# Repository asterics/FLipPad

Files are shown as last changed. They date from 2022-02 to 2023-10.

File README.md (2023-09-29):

# FLipPad

The FLipPad (a.k.a. Flipable Touchpad) is a replacement for a normal PC mouse / keyboard / joystick. 
Instead of moving the mouse/joystick with your hand or pressing keys on a keyboard, the FLipPad can be controlled by very small finger movements.
Unlike a normal Touchpad, the FLipPad can act as mouse, keyboard or joystick - and it can even control bluetooth devices.
For mouse cursor movements, the sensitivity and the operational mode of the FLipPad can be configured, so that finger movements and gestures in the range of millimeters are sufficient to control a computer, smart phone or a complex game.

The clicking functionality is accomplished by tapping, by sip- and puff-activities or via external switches.
All settings and functions of the FLipPad can be tailored to specific capabilities or needs. 
Multiple settings can be stored into the device and changed via finger gestures or other user interactions.
Additional features like built-in environmental control via infrared, optional bluetooth-add-on module for controlling smartphones/tablets or complete software-based control of all functions via serial command interface make the FlipPad one of the most flexible alternative input devices available today.

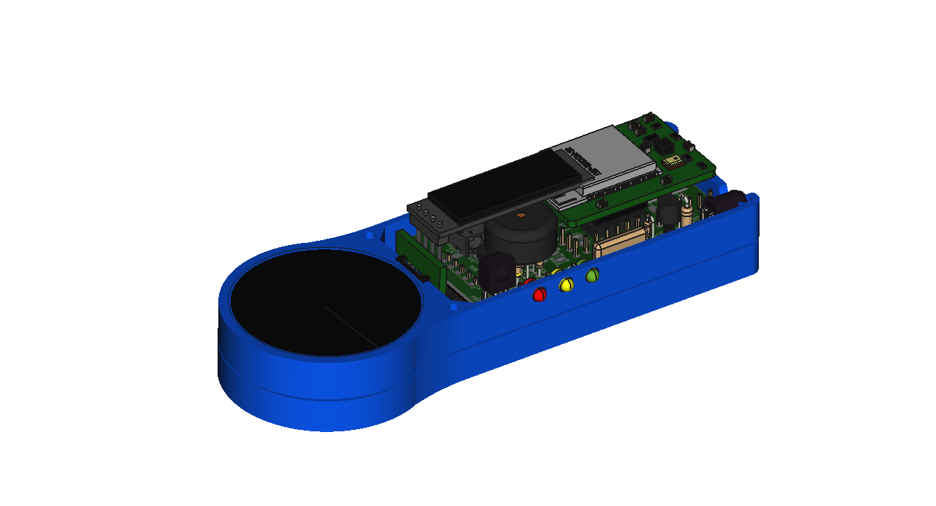
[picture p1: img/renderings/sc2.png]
FLipPad opened - rendered image


The FLipPad was created in course of the [TOM Abraham Accords challenge 2022](https://www.tomchallenge.org/), together with a need-knower who requested and tested this design.
It is based upon the [FlipMouse](https://github.com/asterics/FLipMouse) - a mouth-controller which is also available as Open Source project / DIY-construction kit!

# Software (firmware and configuration manager)

The FLipPad firmware is based on the Arduino/Teensyduino framework. The firmware implements a composite USB HID device (mouse, keyboard, joystick and a serial port in one device).
The mouse and keyboard device classes are used to transmit different keys or mouse actions to the host device. The serial port is used configure the FLipPad (or even use it as a mouse simulator via AT commands).
Multiple configuration settings can be saved (stored in an EEPROM module) and changed via desired user actions.

## Configuration Manager

All settings of the FLipPad can be changed via the [FlipPad Configuration manager](https://flippad.asterics.eu)  
Using the configuration manager in the Chrome web browser, you can assign different actions to all user inputs of the FLipPad.
The Configuration mananger can also be used to update the firmware of the FlipPad and the optional Bluetooth module.

More Information can be found in the user manual: 
* [user manual (english version)](https://github.com/asterics/FLipPad/blob/main/Documentation/UserManual/FLipPadUserManual.md)
* [user manual (german version)](https://github.com/asterics/FLipPad/blob/main/Documentation/UserManual/FLipPadAnwendungsanleitung.md)

## Building the firmware
In order to build the firmware following prerequisites and dependencies must be installed:
* the [Arduino IDE](https://www.arduino.cc/en/software) - use either IDE1 version 1.8.x or IDE2 verison 2.0.x
* the [Teensyduino](https://www.pjrc.com/teensy/td_download.html) add-on (must be compatible with the Arduino IDE version)
* the [SSD1306Ascii](https://github.com/greiman/SSD1306Ascii) library by Bill Greiman (can be installed using Arduino IDE's library manager)
* **important:** in the header file WireKinetis.h (Teensy Wire-library implemenation), *uncomment* the line `//#define WIRE_IMPLEMENT_WIRE1` - should be line number 50, see [here](https://github.com/PaulStoffregen/Wire/blob/2499ec67c2128629ee33697804f8650180293597/WireKinetis.h#L50). 
(This is needed to implement the Wire1 interface, which is disabled by default for the TeensyLC microcontroller in order to save memory.) 
  * If you are using a 1.8.x IDE version under Windows, the file is located inside a subfolder of the Arduino IDE installation, e.g.
`C:/Program Files (x86)/Arduino-1.8.19/hardware/teensy/avr/libraries/Wire/WireKinetis.h` 
  * If you are using a 2.0.x IDE version under Windows, the file is located inside a subfolder of Application Data, e.g.
`C:/Users/<YourName>/AppData/Local/Arduino15/packages/teensy/hardware/avr/1.58.0/libraries/Wire/WireKinetis.h`
* select the *board* 'Teensy LC' in the Arduino IDE tools menu
* select the *USB-type* 'Serial+Keyboard+Mouse+Joystick'  in the Arduino IDE tools menu
* select the correct *Port* after connecting the TeensyLC to your system
* compile and upload the firmware 

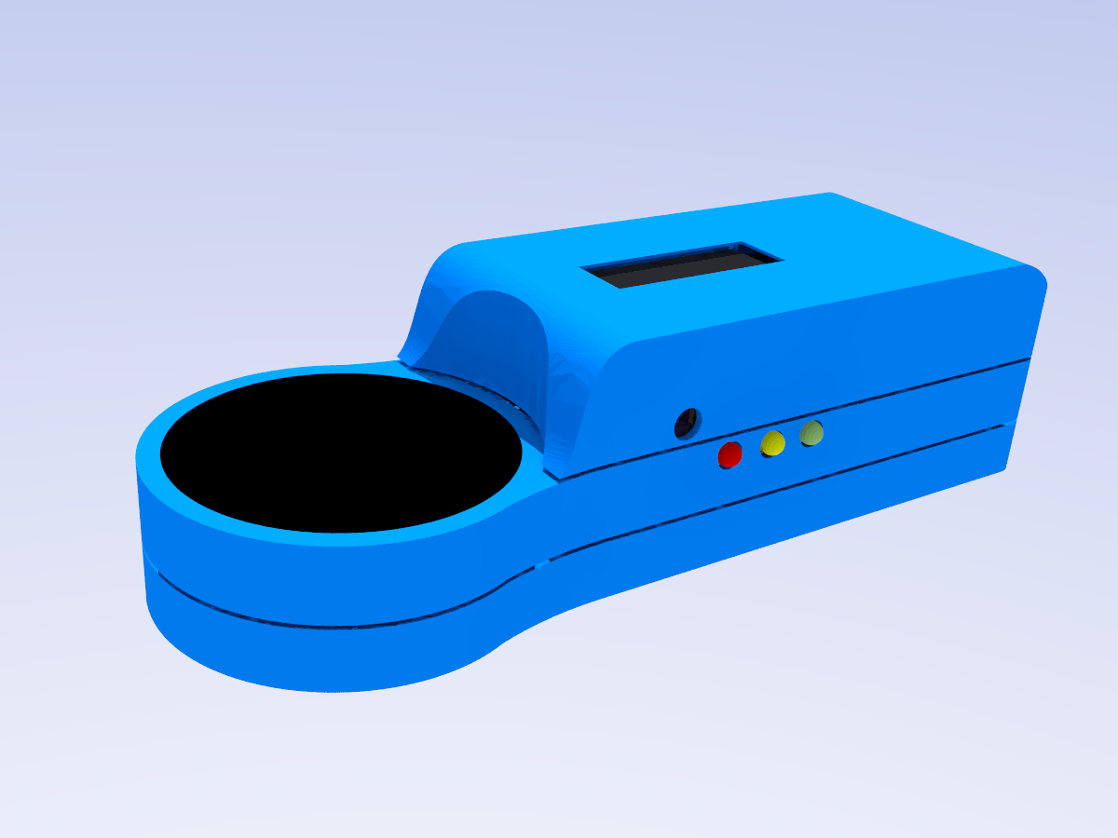
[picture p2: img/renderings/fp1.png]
FLipPad with 3d-printed enclosure - rendered image


# Links and Credits

Most of the work for the FLipPad has been accomplished at the UAS Technikum Wien in course of the R&D-project *WBT* (MA23 project 26-02), which has been supported by the [City of Vienna](https://www.wien.gv.at/kontakte/ma23/index.html),
see: [Webpage WBT project](https://wbt.wien).

Have a look at the [AsTeRICS Foundation homepage](https://www.asterics-foundation.org) and our other Open Source AT projects:

* AsTeRICS: [AsTeRICS framework homepage](http://www.asterics.eu), [AsTeRICS framework GitHub](https://github.com/asterics/AsTeRICS): The AsTeRICS framework provides a much higher flexibility for building assistive solutions. 
The FLipMouse is also AsTeRICS compatible, so it is possible to use the raw input data for a different assistive solution.

* FLipMouse: [The FLipMouse controller](https://github.com/asterics/FLipMouse): an open source alternative input device for controlling computers and mobile devices with minimal muscle movement.

* FABI: [FABI: Flexible Assistive Button Interface GitHub](https://github.com/asterics/FABI): The Flexible Assistive Button Interface (FABI) provides basically the same control methods (mouse, clicking, keyboard,...), but the input
is limited to simple buttons.

* AsTeRICS Grid: [Asterics Grid AAC Web-App](https://grid.asterics.eu): an open source, cross plattform communicator / talker for Augmented and Alternative Communication (AAC).

# Support us
Please support the development of FLipPad by donating to the AsTeRICS Foundation:

<div>
<a title="Donate with PayPal" href="https://www.paypal.com/donate/?hosted_button_id=38AJJNS427MJ2" target="_blank" style="margin-right:3em">
</a>
<span>&nbsp;&nbsp;&nbsp;</span>
<a title="Donate at opencollective.com" href="https://opencollective.com/asterics-foundation" target="_blank">
</a>
</div>

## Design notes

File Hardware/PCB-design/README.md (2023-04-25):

# FLipPad PCB

The main PCB of the FlipPad is compatible with the FLipMouse V2 PCB,
please refer to: https://github.com/asterics/FLipMouse-v2/tree/master/Hardware/PCB-design/Lipmouse_Teensy

__Note:__ Although the PCB is the same, some parts are not placed on the FLipPad PCB. Please refer to the Construction Manual: 
https://github.com/asterics/FLipPad/blob/master/ConstructionKit/ConstructionManual.pdf

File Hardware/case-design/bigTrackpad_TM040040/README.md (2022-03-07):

# Case for TM040040 trackpad

This case version is used for the bigger trackpad from Cirque.
The FreeCAD design in this folder is used for changing/adapting the case.
For renderings and animations, the STL files from this repository are transfered to the
FreeCAD project in the construction manual repo: https://github.com/benjaminaigner/ConstructionManual-FLipPad

To ease up the case design process, the PCBs and external parts are placed in the FreeCAD design.

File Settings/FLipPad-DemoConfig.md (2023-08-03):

## Basic information
This configuration offers 4 modes (slots), demonstrating basic FlipPad settings and operation.
The modes can be changed by pressing Button1.

## Slot1 - "Mouse"
- controls mouse cursor via USB interface
- create mouse clicks via external buttons (button2: hold left mouse button / button3: click right mouse button)
- uses joystick mode (return finger to first touch point or lift finger to stop moving)

## Slot2 - "MousePad"
- controls mouse cursor via USB interface
- create mouse clicks via external buttons (button2: hold left mouse button / button3: click right mouse button)
- uses pad mode (finger movement = cursor movement)

## Slot3 - "MouseBT"
- controls mouse cursor via BT interface 
- uses joystick mode (return finger to first touch point or lift finger to stop moving)
- create mouse clicks via external buttons (button2: hold left mouse button / button3: click right mouse button)
- note that the BT-module must be installed and paired with a BT-capable device

## Slot4 - "Key"
- finger movement creates cursor keys (up / down / left / right) via USB interface
- button2: hold Space key
- button3: hold enter key
- uses sticky pad mode (last finger movement determines key, keys remain sticky)

## for all slots:
- Button1 (internal button): load next slot

## Please note:
- The position correction which is applied after taps and finger gestures only works correctly if the feature "enhance mouse pointer precision" is deactivated, please check the mouse pointer settings of your operating system. Also the overall mouse pointer speed may be adjusted there.

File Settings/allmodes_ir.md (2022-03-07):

## Basic information
This configuration offers 5 modes (slots) for different mouse-pointer, keyboard and infrared actions.
The modes can be changed by triple taps or by pressing Button1/Button3.

## Slot1 - "StickMode"
- controls mouse cursor via USB interface
- uses joystick mode (return finger to first touch point to stop moving)

## Slot2 - "PadMode"
- controls mouse cursor via USB interface
- uses pad mode (finger movement = cursor movement)

## Slot3 - "Phone"
- controls mouse cursor via BT interface 
- uses pad mode (finger movement = cursor movement)
- another tap+down gesture or pressing external button3 creates the keyboard shortcut KEY_GUI + KEY_BACKSPACE which acctivates the Home/Back button in many Android phones
- note that the BT-module must be installed and paired with a BT-capable device

## Slot4 - "GameKey"
- finger movement creates cursor keys (up / down / left / right) via USB interface
- tap creates space key
- uses sticky pad mode (last finger movement determines key, keys remain sticky)

## Slot5 - "TVRemote"
- finger movement up/down: play ir commands "ChnUp" / "ChnDwn" for changing the TV channel 
- finger movement left/right: play ir commands "VolUp" / "VolDwn" for changing the TV volume 

## for all slots:
- Button1 (internal button), Button3 or TripleTap: load next slot
- Button2 or Sip: hold left mouse button (in Slot4: Space Key)
- Puff: click right mouse button (in Slot4: Enter Key)

## Please note:
- The position correction which is applied after taps and finger gestures only works correctly if the feature "enhance mouse pointer precision" is deactivated, please check the mouse pointer settings of your operating system. Also the overall mouse pointer speed may be adjusted there.
- The IR commands "ChnUp", "ChnDwn", "VolUp" and "VolDwn" must be recorded for your device via the WebGui before you can use the "TVremote" actions

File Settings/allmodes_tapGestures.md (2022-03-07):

## Basic information
This configuration offers 4 modes (slots) for different mouse-pointer or keyboard actions.
The modes can be changed by finger gestures (tap + movement), by triple taps or by pressing Button1.

## Slot1 - "StickMode" (double tap + up)
- controls mouse cursor via USB interface
- uses joystick mode (return finger to first touch point to stop moving)

## Slot2 - "PadMode"  (double tap + right)
- controls mouse cursor via USB interface
- uses pad mode (finger movement = cursor movement)

## Slot3 - "Phone" (double tap + down)
- controls mouse cursor via BT interface 
- uses pad mode (finger movement = cursor movement)
- another tap+down gesture or pressing external button3 creates the keyboard shortcut KEY_GUI + KEY_BACKSPACE which acctivates the Home/Back button in many Android phones
- note that the BT-module must be installed and paired with a BT-capable device

## Slot4 - "GameKey" (double tap + left)
- finger movement creates cursor keys (up / down / left / right) via USB interface
- tap creates space key
- uses pad mode (last finger movement determines key)

## for all slots:
- Button 1 (internal button) or tripe tap = load next slot
- Button 2, Sip = hold left mouse button (in Slot4: Space Key)
- Puff = click right mouse button (in Slot4: Enter Key)

## Please note:
The position correction which is applied after taps and finger gestures only works correctly if the feature "enhance mouse pointer precision" is deactivated, 
please check the mouse pointer settings of your operating system. Also the overall mouse pointer speed may be adjusted there.

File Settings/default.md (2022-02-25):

## Basic information
This configuration is the default configuration of the FlipPad.
It offers 4 modes (slots) for different mouse-pointer or keyboard actions.
The modes can be changed by finger gestures (double tap + movement) or by pressing Button1/Button3.

## Slot1 - "StickMode" (double tap + up)
- controls mouse cursor via USB interface
- uses joystick mode (return finger to first touch point to stop moving)

## Slot2 - "PadMode"  (double tap + right)
- controls mouse cursor via USB interface
- uses pad mode (finger movement = cursor movement)

## Slot3 - "Phone" (double tap + down)
- controls mouse cursor via BT interface 
- uses pad mode (finger movement = cursor movement)
- a tap + down gesture creates the keyboard shortcut KEY_GUI + KEY_BACKSPACE which acctivates the Home/Back button in many Android phones
- note that the BT-module must be installed and paired with a BT-capable device

## Slot4 - "GameKey" (double tap + left)
- finger movement creates cursor keys (up / down / left / right) via USB interface
- tap creates space key
- uses pad mode (last finger movement determines key)

## for all slots:
- Button 1 (internal button), Button3 = load next slot
- Button 2, Sip = hold left mouse button (in Slot4: Space Key)
- Puff = click right mouse button (in Slot4: Enter Key)

## Please note:
The position correction which is applied after taps and finger gestures only works correctly if the feature "enhance mouse pointer precision" is deactivated, 
please check the mouse pointer settings of your operating system. Also the overall mouse pointer speed may be adjusted there.

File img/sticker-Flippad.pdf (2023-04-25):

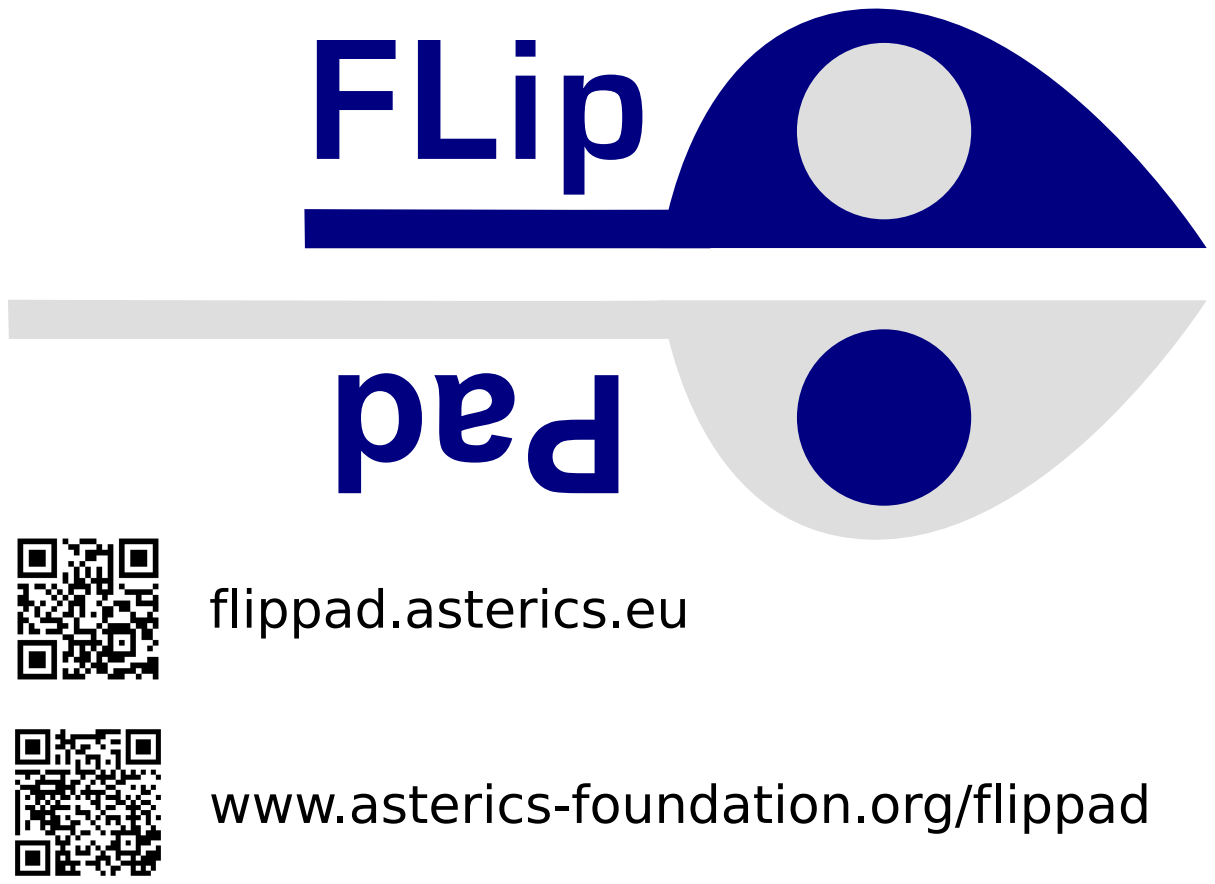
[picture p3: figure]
www.asterics-foundation.org/flippad; flippad.asterics.eu

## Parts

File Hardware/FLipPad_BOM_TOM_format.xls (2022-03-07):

Nr. | Description | Material | Manufacturing Technology | Dimensions | Quantity | Supplier / Purchase Link
1 | Main PCB | FR4 | PCB manufacturing | 61x32x1.6 | 1 | aisler.net (or other PCB manufacturer)
2 | 2x5 2.54mm pin header (male) |  |  | 13x5x16 | 1 | Digikey.com: 952-2124-ND
3 | 100nF ceramic capacitor, 2.5mm pin spacing |  |  | 3x2x3 | 2 | Digikey.com: 478-4855-ND
4 | 1x4 2.54mm pin header (male) |  |  | 13x2.5x16 | 1 | Digikey.com: 732-5318-ND
5 | 1x14 2.54mm pin header (male) |  |  | 36x2.5x16 | 2 | Digikey.com: 732-5325-ND
6 | TeensyLC |  |  | 36x18x4 | 1 | Digikey.com: 1528-2254-ND
7 | 3.5mm jack plugs, 4pin |  |  | 16x7x5 | 2 | Farnell.com: 1216979
8 | SIP resistor network 220R |  |  | 12x2x4 | 1 | Digikey.com: 4605X-101-221LF-ND
9 | 24LC256 EEPROM |  |  | 9x8x4 | 1 | Digikey.com: 24LC256-I/P-ND
10 | TSOP4838 IR receiver |  |  | 7x4x8 | 1 | Digikey.com: TSOP4838-ND
11 | BS170 N-channel MOSFET TO92 |  |  | 5x4x5 | 1 | Digikey.com: BS170_D75ZCT-ND
12 | push button long actuator |  |  | 12x7x7 | 1 | Digikey.com: P10884S-ND
13 | push button short actuator |  |  | 7x7x7 | 1 | Digikey.com: 450-1656-ND
14 | THT resistor 1/8W; 4k7; blue |  |  | 3x1x1 | 4 | Farnell.com: 9343253
15 | THT resistor 1/2W; 12R; brown |  |  | 9x2x2 | 1 | Digikey.com: CFR-50JB-52-12R
16 | 3mm LEDs, red, gren & yellow |  |  | 3x3x5 | 3 | Digikey.com: 160-1708-ND, 160-1946-ND, 160-1710-ND
17 | 5mm IR LED |  |  | 5x5x8 | 1 | Digikey.com: 751-1204-ND
18 | buzzer |  |  | 16x16x8 | 1 | Farnell.com: 1300026
19 | pin spacer | PLA | 3D printed | 3x3x14 | 1 | Self-printed
20 | 1x5 2.54mm pin header (male); 90° |  |  | 9x5x6 | 1 | Digikey.com: 732-5338-ND
21 | Fully assembled FFC adapter PCB |  |  | 19x16x3 | 1 | aisler.net (or other PCB manufacturer with assembly)
22 | 100mm 12pin FFC cable, 0.5mm spacing |  |  | 100x10x0.1 | 1 | Mouser.com: 538-15166-0123
23 | Case-bottom ; bottom part of case | PLA | 3D printed | 36x120x7 | 1 | Self-printed
24 | hot shoe 3/8“ screw | steel |  | 15x15x25 | 1 | https://de.aliexpress.com/item/1005002037418382.html
25 | Case-base ; middle part of case | PLA | 3D printed | 36x120x9 | 1 | Self-printed
26 | OLED 0.91“ SSD1306 |  |  | 38x12x3 | 1 | https://de.aliexpress.com/item/32672229793.html
27 | TM035035 Cirque Trackpad |  |  | 36x36x10 | 1 | Mouser.com: 355-TM0350352024-003
28 | Case-top ; top part of case | PLA | 3D printed | 77x37x18 | 1 | Self-printed
29 | M2x16 (countersunk head) | steel |  | 3x3x17 | 1 | https://de.aliexpress.com/item/1005001971590776.html
30 | Optional: ESP32 addon |  |  | 34x24x12 | 1 | aisler.net (or other PCB manufacturer with assembly)

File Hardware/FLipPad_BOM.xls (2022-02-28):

Device | Package | Parts | Description | Qty | Farnell.com | Digikey.com | RS-Components | aliexpress.com | Others | Pin count | critical mounting Position/direction | Price Single | Price 100 Pieces | all prices excl. VAT (€ if not otherwise noted)
FLIpmouse – electronic parts
31-XX | B3F-31XX | S1 | TE – SPST-NO, short button | 1 | 2452343 | 450-1656-ND | 718-2370 |  |  | 4 | yes | 0.086 | 0.078
31-XX | B3F-31XX | S2 | EVQPF108K SWITCH, long Button | 1 | 2079506 | P10884S-ND | 756-1599 |  |  | 4 | yes | 0.18 | 0.13
FE05-1 | FE05-1 | SV1 | MALE HEADER, 90°, 1x5 | 1 | 2356179 | 732-5338-ND | 828-1667 |  |  | 5 | yes | 0.37 | 0.208
LED3MM | LED3MM | LED1 | LED red – MCL514PD | 1 | 1581128 | 160-1708-ND |  |  |  | 2 | yes | 0.153 | 0.0689
LED3MM | LED3MM | LED2 | LED yellow – MCL514YD | 1 | 1581131 | 160-1946-ND |  |  |  | 2 | yes | 0.249 | 0.0848
LED3MM | LED3MM | LED3 | LED green – MCL514GD | 1 | 1581130 | 160-1710-ND |  |  |  | 2 | yes | 0.198 | 0.0848
MA05-2 | MA05-2 | AUX | MALE HEADER, 2x5; Harwin M20 | 1 | 1022236 | 952-2124-ND |  |  |  | 10 | - | 0.258 | 0.222
RN04 | RN-5 | RN1 | Resistor network, 220R | 1 | 2333623 | 4605X-101-221LF-ND |  |  |  | 5 | yes | 0.362 | 0.153
TeensyLC – pin header | MA14-1 | -- | MALE HEADER, 1x14 | 2 | 2356164 | 732-5325-ND |  |  | Alternative: 2356174 (farnell) / 732-5333-ND (digikey) For all 3 pin headers | 14 | - | 1.77 | 0.896
TeensyLC – pin header | MA05-1 | -- | MALE HEADER, 1x5 | 1 | 2356157 | 732-5318-ND |  |  |  | 5 | - | 0 | 0
C-EU025-025X050 | C025-025X050 | C1,C2 | 100nF capacitor | 2 | 2112751 | 478-4855-ND |  |  |  | 2 | - | 0.21 | 0.121
1503_02 | 1503_02 | X1,X2 | Jack plugs JISC 6560 | 2 | 1216979 |  |  |  |  | 4 | yes | 2.82 | 2.28
24LC256P | 24LC256P | IC1 | I2C EEPROM | 1 | 9757970 | 24LC256-I/P-ND | 454-371 |  |  | 8 | yes | 0.84 | 0.681
R-EU_0309/V | 0309V | R1,R2,R3,R11 | 4k7, blue, | 4 | 9343253 |  |  |  |  | 2 | - | 0.174 | 0.0765
LED5MM | LED5MM | LED5 | LED | 1 | 3152856 | 751-1204-ND | 699-7635 (or 50pcs: 818-7663) |  |  | 2 | yes | 0.122 | 0.104
R-EU_0309/V | 0309V | R12 | 12R, min 0.25W | 1 | 9338420 | CFR-50JB-52-12R |  |  |  | 2 | - | 0.061 | 0.04
Piezo buzzer | EFBAA40D101 | SG1 | piezo buzzer | 1 | 1300026 |  | 457-011 |  | Cheaper at rs-components | 2 | - | 0.61 | 0.51
TSOP4838 | TSOP2XXX | U3 | TSOP4838 | 1 | 4913190 | TSOP4838-ND | 708-5115 (or 90pcs: 919-0014) |  |  | 3 | yes | 1.06 | 0.539
BS170 | TO-92 | Q1 | N-MOS FET, BS170 | 1 | 2453831 | BS170_D75ZCT-ND | 671-4736 |  |  | 3 | yes | 0.138 | 0.138
FlipPad daughterboard & mechanical parts
header 5pol | FE05-1 | SV1 | FEMALE HEADER, 1x5 | 1 |  | SAM1122-05-ND |  |  | Alternative: 9728910 (Farnell, for 7) | 5 | yes | 0.9028571429 | 0.75
Glide trackpad (TM035035) |  |  |  | 1 |  |  |  |  | mouser: 355-TM0350352024-003 |  |  | 7.7 | 5.5
glide_adapter – PCB |  |  |  | 1 |  |  |  |  | see the glide_adapter PCB & BOM |  |  | 5 | 1
OLED SSD1306 – 0.91“ |  |  |  | 1 |  |  |  |  | order at Aliexpress, Azdelivery or Amazon |  |  | 1 | 0.8
Spacer – adjusting pin header/LEDs | -- | -- | -- | 1 |  |  |  |  | self printed | 5 | - | 0.35 | 0.2
Flipmouse Teensy, PCB | -- | -- | -- | 1 |  |  |  |  | PCBPool, etc. | - | - | 8 | 3.44
TEENSYLC | TEENSY_3.1_BASIC | TEENSYLC | TeensyLC | 1 |  | 1568-1233-ND |  |  | watterott.com (or: PJRC.com) | 33 | yes | 12.5 | 12.5
Hot shoe adapter (mounting) | -- | -- | -- | 1 |  |  |  | Search for „3/8" hot shoe mount“ | Amazon: B00RSXM3U2 | - | - | 2.18 | 1.2
USB cable | -- | -- | -- | 1 | -- | -- |  | Search for „MicroUSB cable 1m“ |  | -- | -- | 2 | 2
USB stick | -- | -- | -- | 1 | -- | -- |  | Search for „8GB USB Stick orange“ |  | -- | -- | 4 | 3
Packaging | -- | -- | -- | 1 | -- | -- |  | -- | -- | -- | -- | 6 | 6
Parts ONLY for 3D printed case
M2x16 screw | -- | -- | -- | 2 | 7070585 | 36-29341-ND |  |  |  | - | - | 5.68 | 0.2272
3D printed case (3 parts) | -- | -- | -- | 1 |  |  |  |  |  | - | - | 3 | 2
 |  |  |  |  |  |  |  |  |  |  | Sum: | 67.97 | 45.03
 |  |  |  |  |  |  |  |  |  |  | Shipping costs: | 25.00 | 0.25
Packing material (box for kit) |  | Stülpkarton |  | 1 |  |  |  |  | Ratioform 167-5w |  |  | 1.69 | 1.39
Packing material (send carton) |  | Verpackungskarton |  | 1 |  |  |  |  | Ratioform W129 |  |  | 0.55 | 0.51
 |  |  |  |  |  |  |  |  |  |  | TOTAL (3D print): | 114.26 | 56.62
 |  |  |  |  |  |  |  |  |  |  | Including 20% VAT

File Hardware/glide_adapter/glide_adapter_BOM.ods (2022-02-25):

Reference | Value | Footprint | Datasheet | Mouser | Notes
J2 | Conn_01x12_Female | Connector_FFC-FPC:Hirose_FH12-12S-0.5SH_1x12-1MP_P0.50mm_Horizontal | ~ | 798-FH12-12S-0.5SH55
J1 | Conn_01x05_Female | Connector_PinSocket_2.54mm:PinSocket_1x05_P2.54mm_Vertical | ~ | DON'T ORDER (437-8018700510001101) | normally, a connector is available in your lab or the FlipMouse construction kit.
R1,R2 | 4k7 | Resistor_SMD:R_0805_2012Metric_Pad1.20x1.40mm_HandSolder | ~ | 603-AC0805FR-7W4K7
J3 | Conn_01x04_Female | Connector_Harwin:Harwin_M20-89004xx_1x04_P2.54mm_Horizontal | ~ | 801-87-004-40-002101
C1 | 1u | Capacitor_SMD:C_0805_2012Metric_Pad1.18x1.45mm_HandSolder | ~ | 710-885012207051
-- | Trackpad | TM035035-2024-003 (currently only available case) |  | 355-TM0350352024-003 | Select one here: https://www.mouser.at/new/cirque/glidepoint-circle-trackpads/
 | FFC cable | FPC cable, 12pol. Same side contacts, 76mm |  | 538-15166-0121

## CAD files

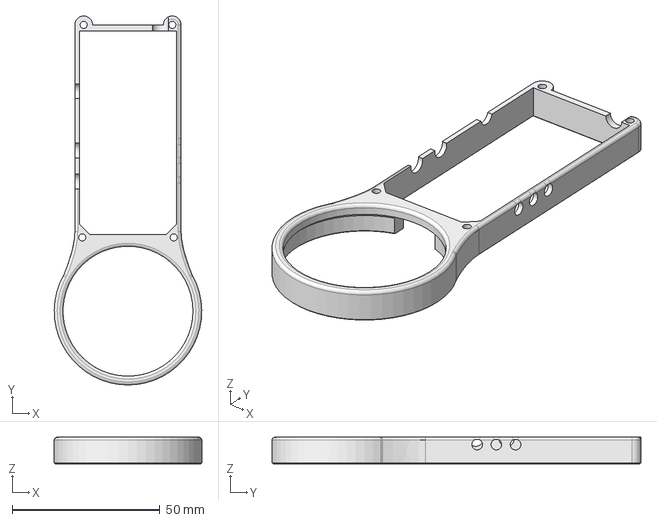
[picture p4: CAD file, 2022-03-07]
Hardware/case-design/bigTrackpad_TM040040/case_TM040040.FCStd
50.0 x 125.0 x 9.00 mm

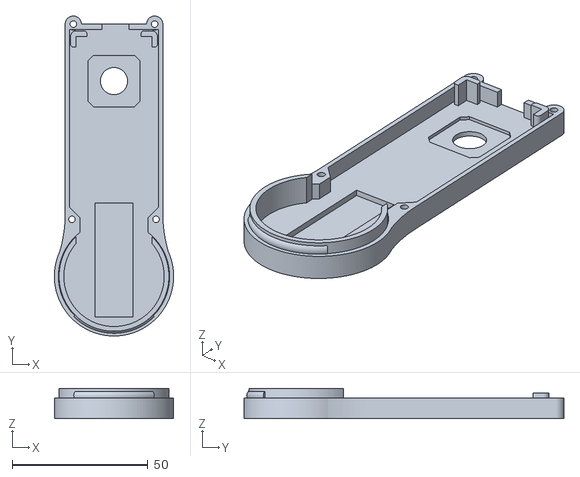
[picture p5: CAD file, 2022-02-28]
Hardware/case-design/smallTrackpad_TM035035/case_TM035035-bottom.stl
44.0 x 118.0 x 11.1

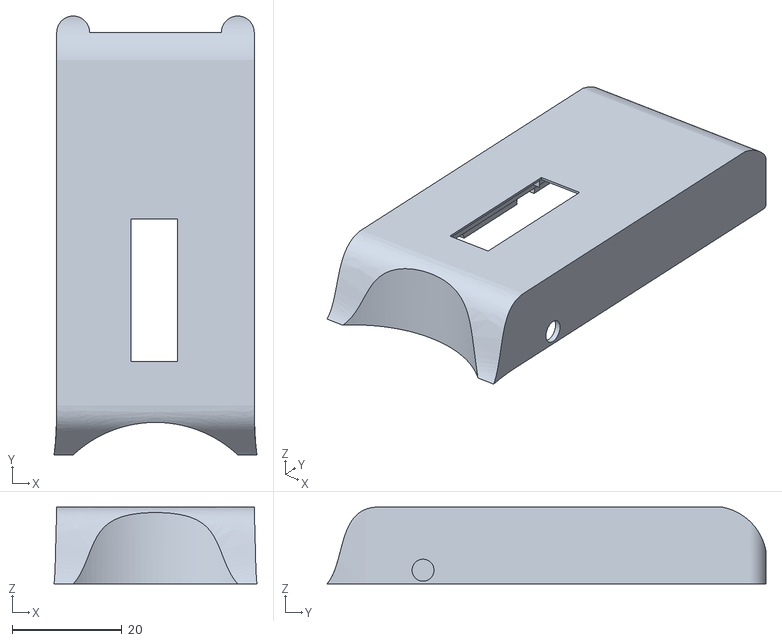
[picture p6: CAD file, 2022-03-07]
Hardware/case-design/bigTrackpad_TM040040/case_TM040040-top.stl
37.0 x 80.0 x 14.0

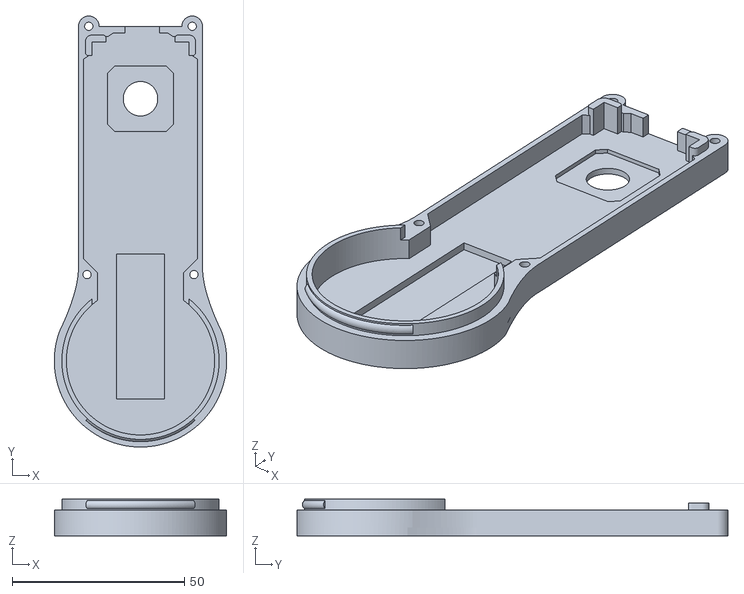
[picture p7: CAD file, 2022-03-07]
Hardware/case-design/bigTrackpad_TM040040/case_TM040040-bottom.stl
50.0 x 125.0 x 10.7

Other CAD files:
Hardware/case-design/bigTrackpad_TM040040/case_TM040040-base.stl

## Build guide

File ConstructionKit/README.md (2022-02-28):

# ConstructionManual

This construction manual contains instructions how to build the FlipPad.

**Have fun !!**

## Sources

Due to the size of the raw material, the sources for the PDF manual are located here: https://github.com/benjaminaigner/ConstructionManual-FLipPad

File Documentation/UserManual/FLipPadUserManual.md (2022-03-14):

# FLipPad - Finger Trackpad

**User Manual v3.1, AsTeRICS Foundation**

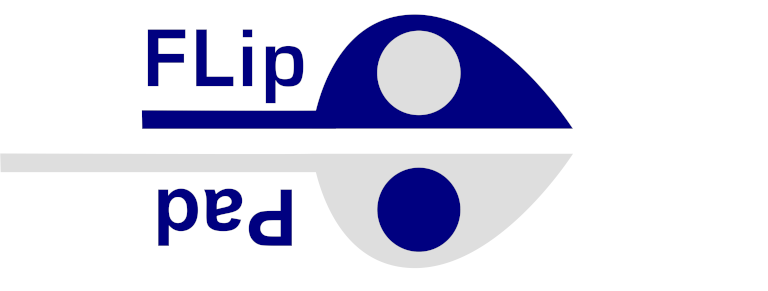
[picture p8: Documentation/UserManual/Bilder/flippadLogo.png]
FLipPadLogo


**Table of Contents**

[TOC]

____

# Preface

The FLipPad is an open source Assistive Technology module which is developed at the [University of Applied Sciences Technikum Wien](https://www.technikum-wien.at) and delivered as a DIY-construction kit by the [AsTeRICS Foundation](https://asterics-foundation.org). The FLipPad allows people who cannot use standard computer input devices to control a computer mouse cursor or a joystick as well as typing desired keyboard keys or using infrared remote controls. The FLipPad device can be actuated with minimal finger movements and/or external buttons. Sip & puff actuation is possible, but optional.

The FLipPad can be configured via a web-based configuration application which is called *configuration manager* from now on. It can be found at the website [flippad.asterics.eu](https://flippad.asterics.eu). This user manual includes a description of the configuration manager and explains how to use  the different functions and features of the FLipPad. The FLipPad can be used on any Windows-, Mac- or Linux-computer without installation of special software, because it behaves like a standard mouse / joystick / keyboard device. By using the optional Bluetooth Add-On module, smart phones or tablet computers can be controlled - which will also be explained in this manual. 

All design files for the electronics and the 3D-printed enclosure - as well as the software source code - are available as open source and are distributed via the AsTeRICS Foundation website and via GitHub. The construction kit for the FLipPad can be purchased from [Hackerspaceshop.com](https://hackerspaceshop.com/collections/FLipPad). Detailed instructions are provided in the [FLipPad construction manual](https://github.com/asterics/FLipPad/blob/master/ConstructionKit/ConstructionManual.pdf). Have fun building and using your FLipPad!

The AsTeRICS Foundation

[www.asterics-foundation.org](https://asterics-foundation.org/)

# Hardware overview

The FLipPad is available with a 3D-printed enclosure. Design files for the 3D-printed case are provided in the [Github repository](https://github.com/asterics/FLipPad/tree/main/Hardware/case-design). The primary method for interacting with the FLipPad is the black trackpad, which can either be a 35mm or a 40mm type.

<p align="left" width="100%">
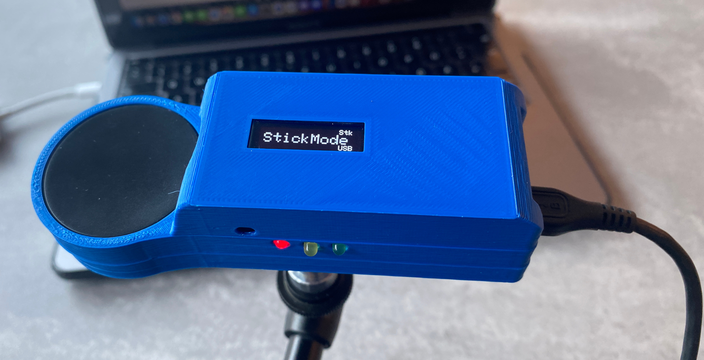
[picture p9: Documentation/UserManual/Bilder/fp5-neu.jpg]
    
</p>

*Figure 1*: The FLipPad device

Additionally, two external momentary switches can be attached to the jack plug connectors on the left side of the FLipPad enclosure and one button is already integrated on the device ("B1", see Figure 3).

**Users can interact with the FLipPad in several ways:**

1. by touching the trackpad and moving the finger
1. by tapping the trackpad once or more
2. by actuating (up to) 3 momentary switches / pushbuttons

**The hardware features of the FLipPad:** (see pictures at the bottom of this list)

(a)    One built-in switch (“Button 1 / B1”) on the device, e.g. to change the active configuration ("slot")

(b)    Two 3.5 mm jack plug sockets for attaching external switches to trigger additional functions (“Button 2 / B2” and “Button 3 / B3”)

(c)    3 Indicator Light Emitting Diodes (LEDs) for showing the active configuration, calibration procedure etc.

(d)    Universal infrared remote control receiver and transmitter

(e)    “Hot Shoe” Adapter for mounting to a Manfrotto Magic Arm or similar mounting system (3/8" screw)

(f)    Firmware upgrade via FLipPad web application on [FLipPad.asterics.eu](FLipPad.asterics.eu)

(g)    Optional add-on board for Bluetooth (e.g. to control smartphones or iOS devices)

<p align="left" width="100%">
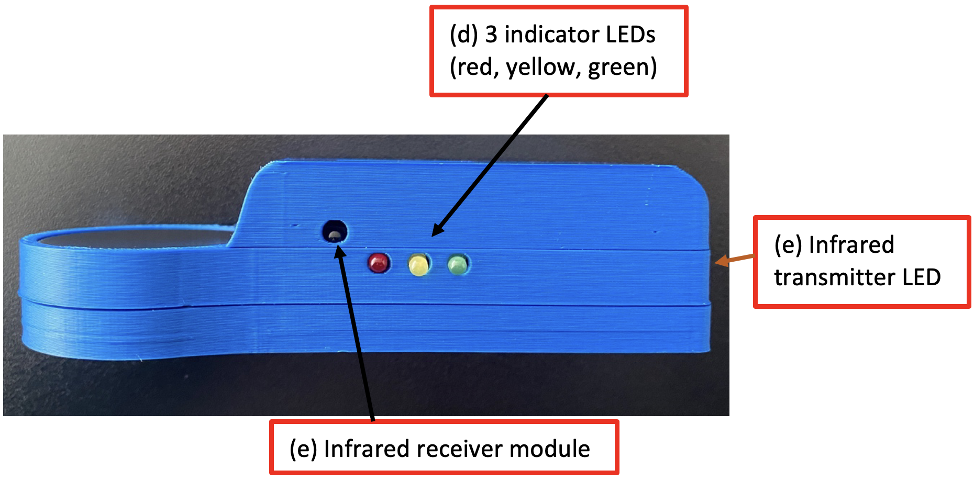
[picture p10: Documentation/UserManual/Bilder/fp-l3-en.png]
    
</p>

*Figure 2*: FLipPad right side

<p align="left" width="100%">
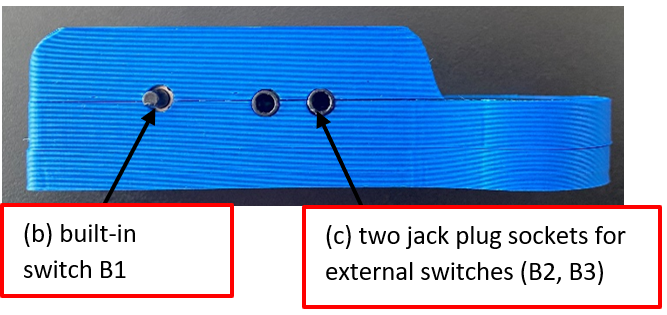
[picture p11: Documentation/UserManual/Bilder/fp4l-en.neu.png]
    
</p>

*Figure 3*: FLipPad left side

On the right side of the FLipPad enclosure, 3 LEDs indicate the current mode of operation (which can be changed to activate different speed settings or functional options). Furthermore, the Infrared (IR-) receiver module is accessible here. This modules can be used for recording arbitrary infrared remote control commands (for example to change volume or channel settings of a TV-set). The IR-signals can then be replayed from the IR-emitting diode at the rear side of the FLipPad.

The left side of the FLipPad gives access to a button (B1) which offers a configurable function (for example changing the operational mode).
Two 3,5mm Jack Plug sockets marked (B2) and (B3) allow the connection of external momentary switches. Standard switches with 3,5 mm mono jack plugs can be used.

## Bluetooth – Add-On Module

The optional Bluetooth Add-On module allows connection of the FLipPad as a Bluetooth mouse/keyboard to various mobile devices (smartphones, tablets, IOs devices). If this module is not contained in the DIY-Kit, it can be ordered individually from the AsTeRICS Foundation or built from the hardware design files available on Github (parts must be ordered individually). If you are interested in this feature, have a look at the [esp32_mouse_keyboard](https://github.com/asterics/esp32_mouse_keyboard/tree/master/hardware) repository where construction of the Add-On module is explained.

<p align="left" width="100%">
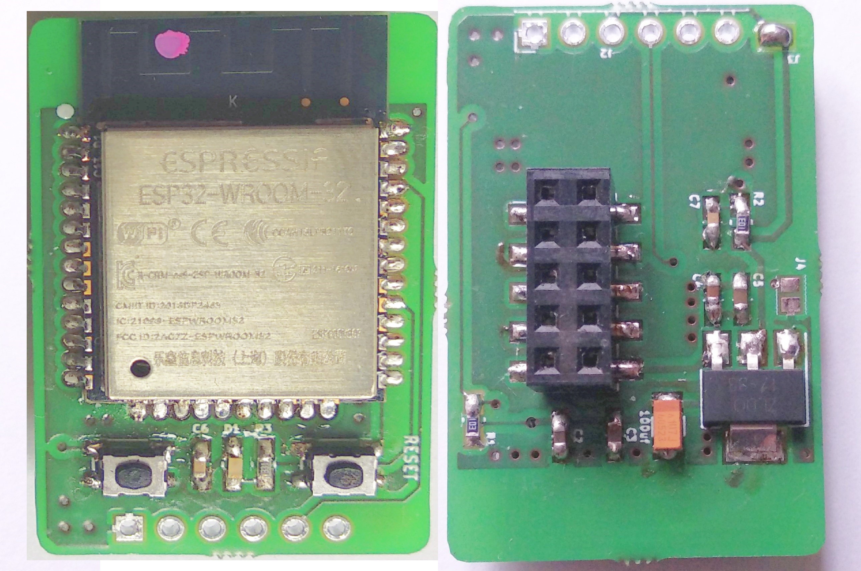
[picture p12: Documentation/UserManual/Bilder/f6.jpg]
    
</p>

*Figure 5*: Bluetooth Add-on Module

# Instructions for proper mounting and use

**1. Mount the FLipPad device appropriately for the user**
<p align="left" width="100%">
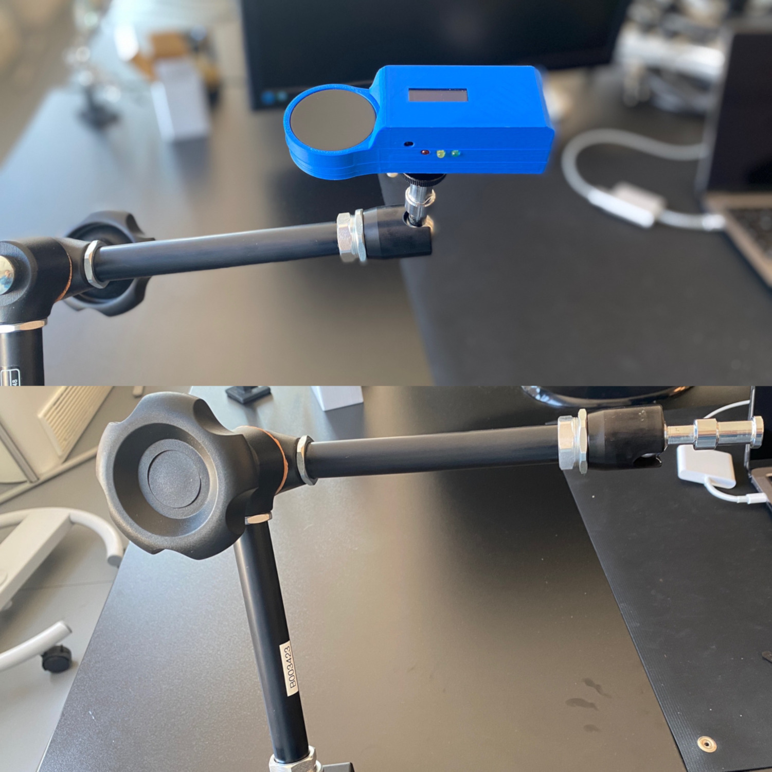
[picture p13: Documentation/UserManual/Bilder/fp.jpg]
    
</p>

*Figure 7*: Mounting the FLipPad

The picture shows a “[Manfrotto Magic Arm](https://www.manfrotto.com/global/magic-photo-arm-smart-centre-lever-and-flexible-extension-143n/)” + ”[SuperClamp](https://www.manfrotto.com/global/super-photo-clamp-without-stud-aluminium-035/)” mount combination. You could also use the [Manfrotto Gelenkarm](https://www.manfrotto.com/global/single-arm-2-section-196ab-2/) or any other kind of mounting solution which fits to the HotShoe-Adapter of the FLipPad. Be careful when attaching the mount to the 3/8” screw of the HotShoe-Adapter: hard forces might break the enclosure of the device. 

<p align="left" width="100%">
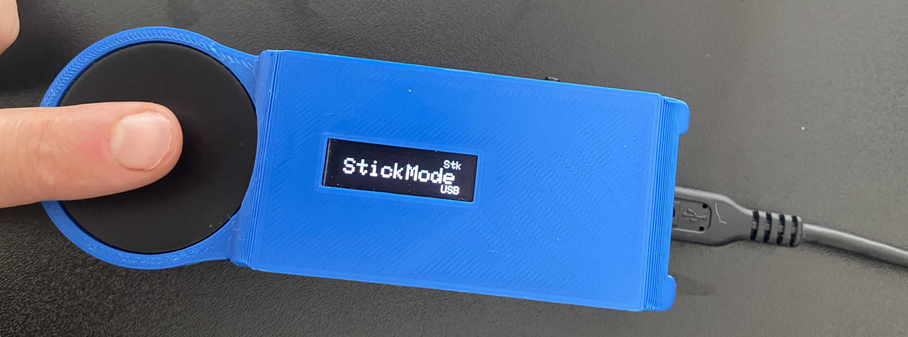
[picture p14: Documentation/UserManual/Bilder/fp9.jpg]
    
</p>

*Figure 9*: Using the FLipPad with fingers

If the user desires to actuate the FLipPad with a finger or the thumb the system appropriately so that the hand is in a resting position and the finger can touch the joystick without stress. Attach one or two additional external switches if desired, and mount the switches at suitable locations.

**2. Attaching the FLipPad to a Computer, Tablet or Smart Phone**

When connecting the FLipPad via the provided USB-micro cable, do not touch the mouthpiece as long as the LEDs are blinking (the initial blinking indicates the zero point calibration phase). Wait until the device is recognized by the computer, then touch the trackpad and move your finger to see if the device is working.

ball-switch

*Figure 11*: Connecting the FLipPad with the computer

**Please note** that every time you apply power to the FLipPad device (respectively when you plug it in) the **zero-calibration is performed which is indicated by blinking all 3 LEDs**. It is important that you do not touch the trackpad until the LEDs stopped blinking. 

#### Using the FLipPad with Smart Phones or Tablets that provide USB-OTG

The FLipPad should work with any operating system which supports USB HID (Mouse/Keyboard/Joystick) devices, such as Windows, Linux or MacOS. Several Android devices provide an USB port with USB-OTG (“on-the-go”) functionality. If your device supports “OTG” you can attach the FLipPad using an USB-OTG-adapter (see picture below) and it should work as a normal mouse (you will get a mouse cursor) or keyboard. You can test if your Android phone or tablet features the USB-OTG function with the “OTG checker” app.

<p align="left" width="100%">
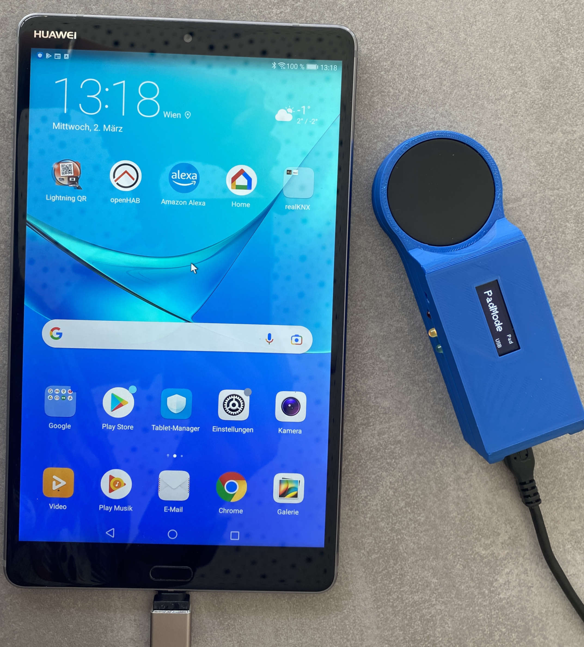
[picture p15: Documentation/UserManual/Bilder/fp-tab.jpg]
    
</p>

*Figure 12*: Using the FLipPad with the Smart Phone

#### Using the FLipPad via Bluetooth

The Bluetooth – Add-On-module for the FLipPad allows wireless mouse/keyboard control of computers, tablets and smart phones. Furthermore, iPhones or iPads can be used via VoiceOver & assistive switch support. For more information see chapter [*Using the Bluetooth Module*](https://github.com/asterics/FLipPad/blob/master/Documentation/UserManual/Markdown/FLipPadUserManual.md#using-the-bluetooth-module).

# The FLipPad Configuration Manager

The [FLipPad Configuration Manager](https://flippad.asterics.eu/index_pad.htm) offers a Graphical User Interface (GUI) to change and store settings of the FLipPad device so that all features and functions can be adapted to personal preferences and needs. **Currently, the Google Chrome browser (or a Chromium-based browser) must be used.** The Configuration Manager is accessible by entering the following website: **https://flippad.asterics.eu**. The FLipPad Configuration Manager sends and receives information from/to the FLipPad. This information transfer occurs through a communication port (COM port). 

The following figure shows the welcome page of the FLipPad Configuration Manager: 

<p align="left" width="100%">
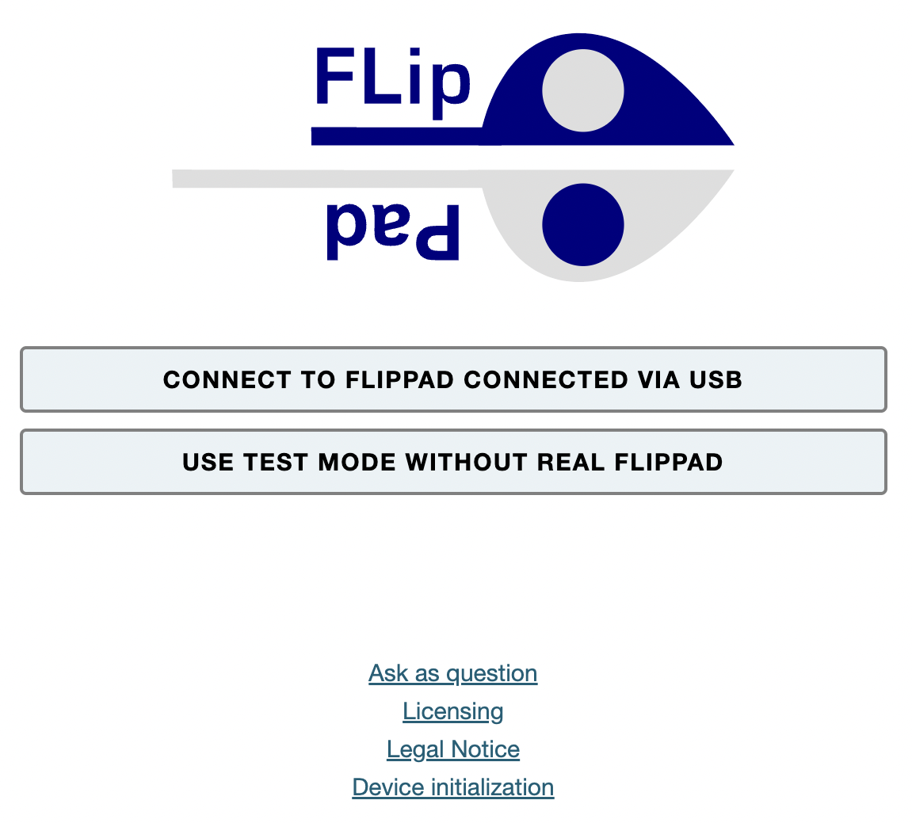
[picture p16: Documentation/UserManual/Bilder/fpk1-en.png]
    
</p>

*Figure 13: Welcome page of the FLipPad Configuration Manager*

### Connecting the FLipPad Device

To connect the device, follow these steps:

1. Make sure your device is connected to your computer via an USB port (see page "Instructions for proper mounting and use"). 
2. Click CONNECT TO FLIPPAD CONNECTED VIA USB and select the appropriate COM port (communication port) in the selection box. If the selection box appears empty, this means that no communication port has been detected. In this case, please reconnect the FLipPad device and wait for the COM port to be updated.
3. Once the COM port is selected, click the “Connect” button at the bottom of the selection box. 
4. After successful connection of the COM port, the main window (see Figure 14) will be displayed and you should see live feedback of the stick movement. The port status at the top right corner of the window will show “connected”.

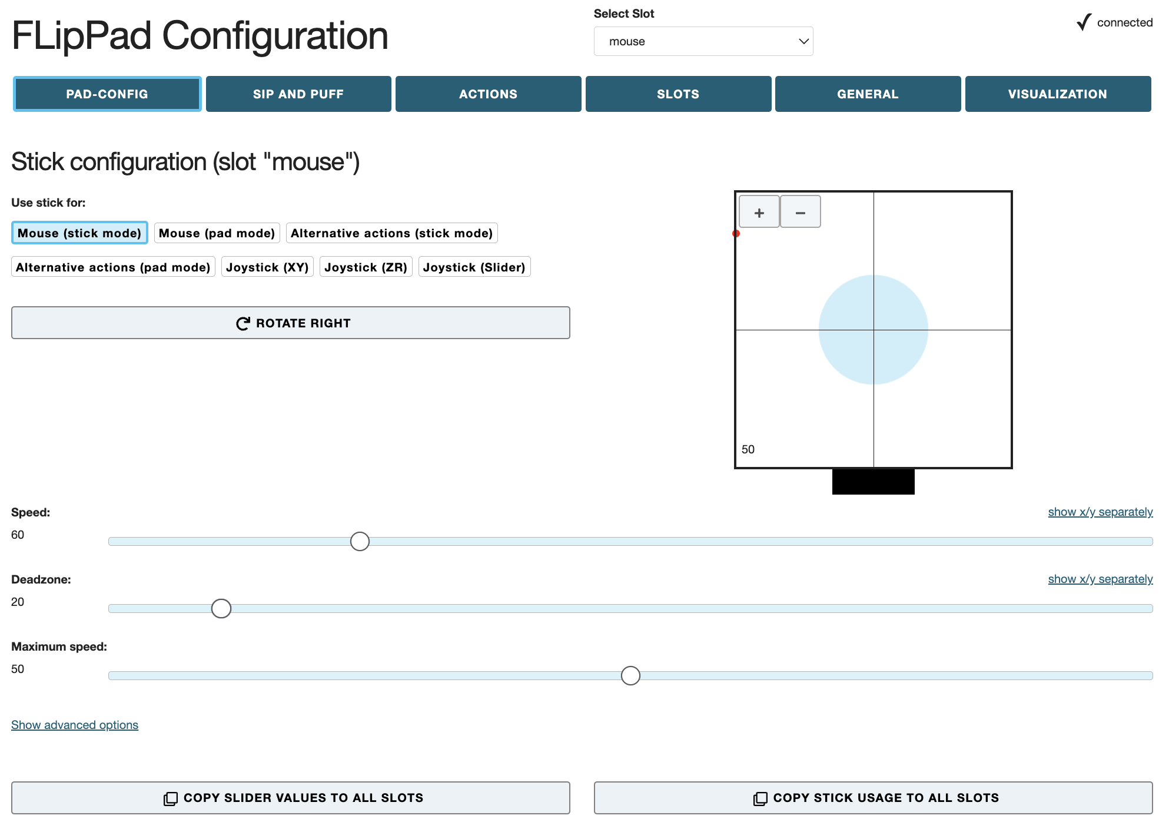
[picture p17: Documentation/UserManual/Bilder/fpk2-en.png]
ConfigManager


*Figure 14: FLipPad Configuration Manager*

## Changing Settings and Features

### Operational modes – “memory slots”

The FLipPad Configuration Manager allows adjustment of all important settings (operational modes). The settings are stored in individual **memory slots** (for example one slot for fast mouse operation, one slot for slow mouse operation, one slot for keyboard key generation etc.). All settings can be stored into (or loaded from) the FLipPad device. The settings can also be saved to (or loaded from) a file on your computer. 
Settings which were stored into the FLipPad stay valid also if the power supply / USB cable is removed. When the FLipPad is plugged in the next time, the settings will be available – also if you use another computer or operating system!

### PAD Configuration (Tab PAD-CONFIG)

Using the PAD-CONFIG tab of the FLipPad Configuration Manager, you will be able to change the *Speed, Deadzone* and *MaximumSpeed* of the FLipPad pad. Furthermore, you can change *Acceleration, Trackpad sensitivity*, *Maximum tap duration* and *Maximum duration of Tap + Slide gestures* - these settings are visible only if you activate *“Show advanced options”*. 

#### Define pad usage (“Use pad for”)

On the top of the PAD-CONFIG tab, the primary function of the pad can be chosen. By default, the pad is creating mouse cursor movements. However, the pad can also be used for alternative actions (such as pressing the key ‘A’ when the pad is pushed up), which can be specified in the ACTIONS tab (see section [*Assignment of different actions*](https://github.com/asterics/FLipPad/blob/master/Documentation/UserManual/Markdown/FLipPadUserManual.md#assignment-of-different-actions-tab-actions). Furthermore, the pad can emulate a real joystick or gamepad  (see section [*Using the stick for Joystick movement*](https://github.com/asterics/FLipPad/blob/master/Documentation/UserManual/Markdown/FLipPadUserManual.md#using-the-stick-for-joystick-movement). 

#### Pad Orientation (Change with click on “ROTATE RIGHT”)

The FLipPad is mounted using a HotShoe 3/8” mounting screw which is located on the button of the FLipPad case. The orientation can be changed according to the user’s preferences. If the FLipPad is mounted e.g. upside-down, the stick orientation can be selected accordingly so that the up/down/left/right movements are still interpreted correctly. A click on “ROTATE RIGHT” changes the orientation by 90°. Orientation settings for 0 / 90 / 180 and 270 degrees are possible, so that any mounting orientation is possible.

<p align="left" width="100%">
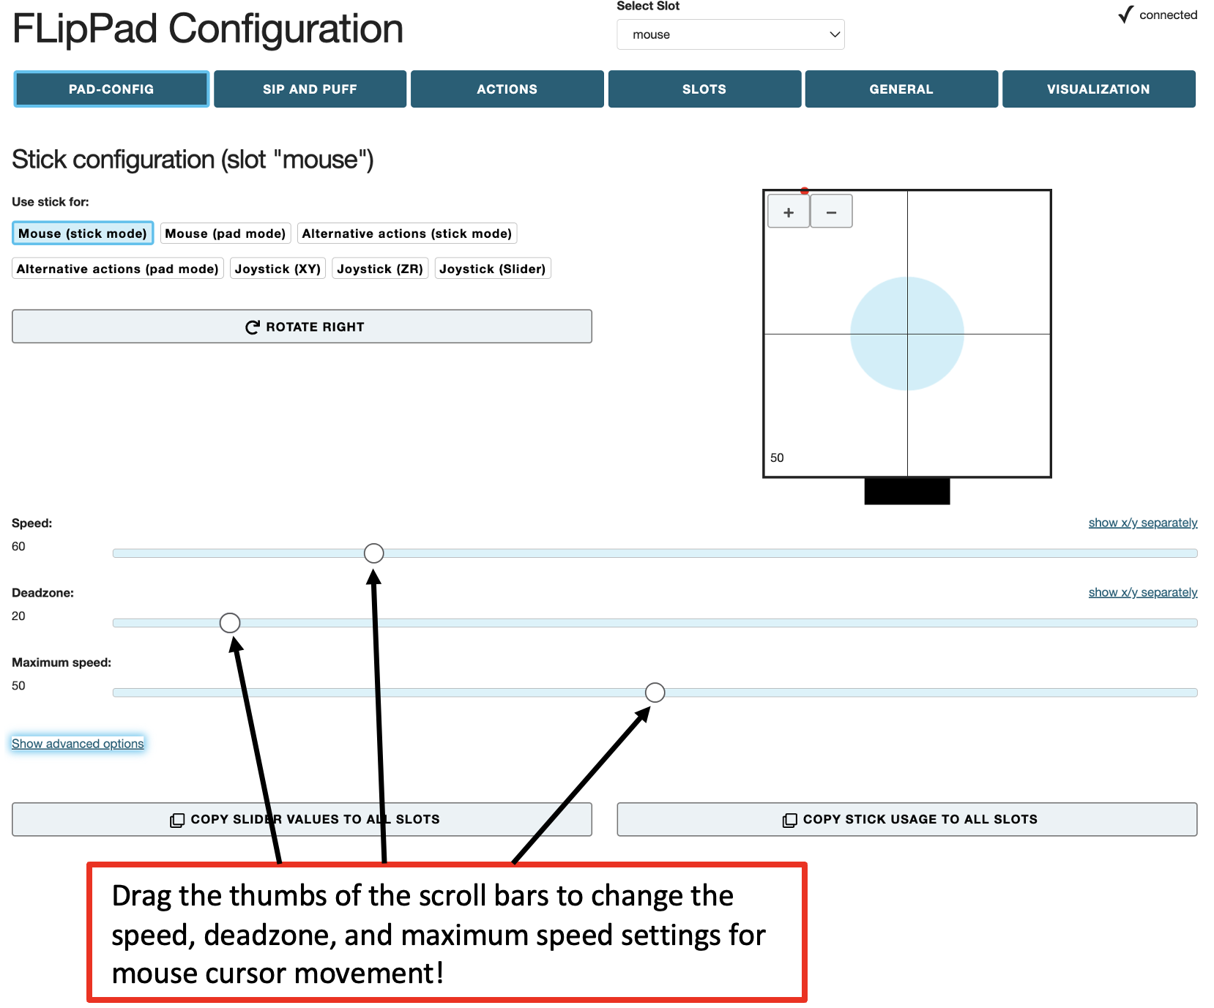
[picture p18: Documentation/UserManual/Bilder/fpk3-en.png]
    
</p>

*Figure 15: FLipPad Configuration Manager: Tab PAD-CONFIG, Scroll bars*

The scroll bars allow changing the parameters of the stick and the behavior of the mouse cursor according to the preferences of the user. The behavior of the following characteristics can be changed: 

#### Sensitivity

When using the stick for cursor movement, the sensitivity of the stick can be adjusted via the *Sensitivity* scroll bar. A smaller value results in slower cursor movement. To change the value, click and drag the scroll bar knob or click the bar next to the knob. 

#### Deadzone

The *deadzone* setting defines a passive zone for the stick movements: when the deadzone value is low, very slight stick movements will already cause cursor movement (or execute the assigned alternative function – see chapter *Assignment of different actions*). If the deadzone setting is too low, the cursor starts unintended drifting. In this case, increase the deadzone value so that cursor drifting does not occur under normal operating conditions for a given user. (However, for some users it could be desired to use a very small deadzone in order to allow cursor movments with minimal finger movement). For alternative actions (such a key presses), it makes sense to use a bigger deadzone value in order to avoid unintended actions.

#### Split axis control for sensitivity and deadzone

If desired, the sensitivity- and deadzone-values for horizontal or vertical movements can be changed individually. In order to do that, select “*show x/y separately*”, as shown below: 

<p align="left" width="100%">
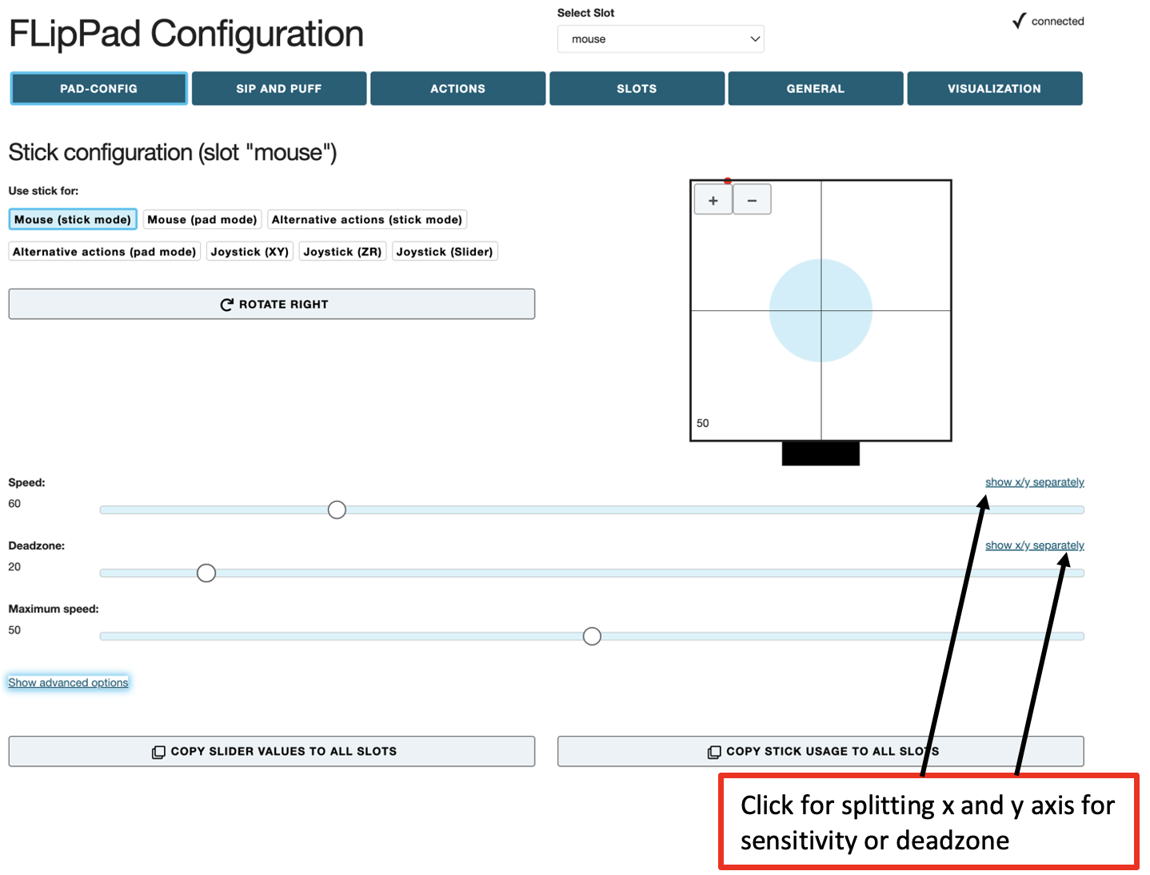
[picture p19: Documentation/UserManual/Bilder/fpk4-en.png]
    
</p>

*Figure 16: FLipPad Configuration Manager: Tab PAD-CONFIG, splitting x/y*

#### Maximum Speed

Turning the maximum speed setting to a low level is useful if a user desires to limit the cursor speed, keeping high sensitivity / acceleration.

**“Show advanced options”**:

#### Acceleration

This setting is enabled by clicking *"Show advanced options"*. The acceleration setting allows influencing the acceleration behavior of the mouse cursor: if acceleration is set to a low level, even a strong finger movement will start a slow (but progressing) cursor movement which makes it easier to reach small targets precisely.

### Using the Pad for Joystick Movement

If you select one of the joystick modes in the PAD-CONFIG tab, moving the FLipPad  up / down / left / right will result in joystick activities. The FLipPad will behave like a gamepad with 6 axes (*X/Y*, *Z/Z-Turn* and *Slider1/Slider2*). As the FLipPad can only deliver 2 axes of information at a time, the desired joystick axis must be selected.

<p align="left" width="100%">
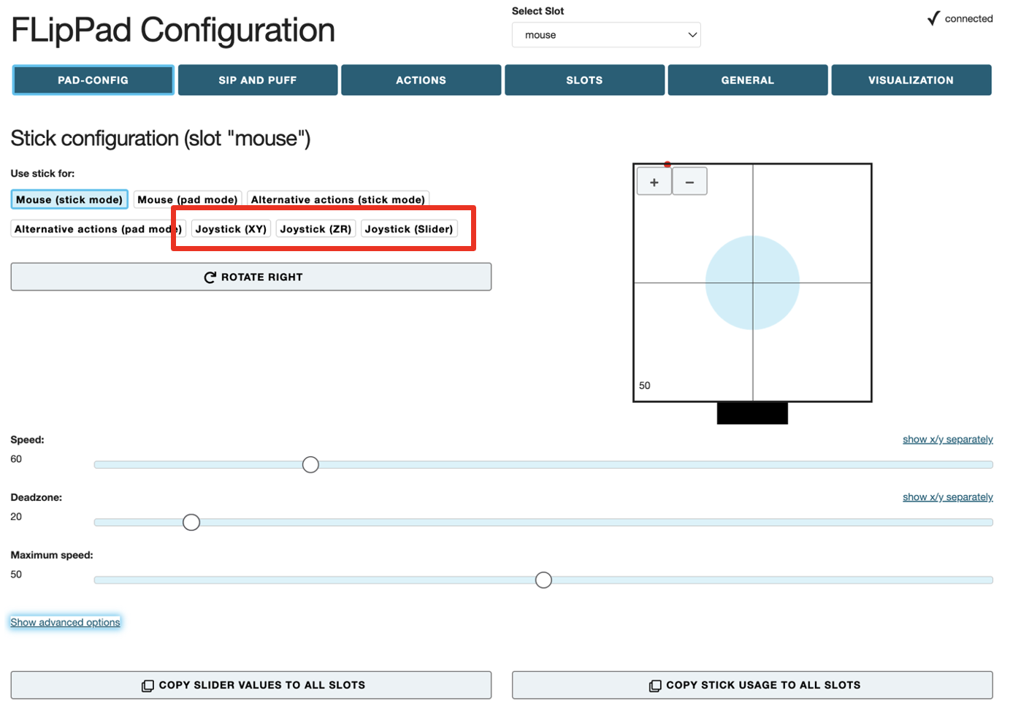
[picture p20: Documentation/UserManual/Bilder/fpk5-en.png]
    
</p>

*Figure 18: Set pad configuration for joystick movement*

Please note that the joystick function must be supported by software applications running on the computer (for example computer games). Microsoft Windows offers a test software called “*joy.cpl*” – you can start this utility by entering “*joy.cpl*” into the search dialog. 

The joystick controller provided by the FLipPad is called *“Serial+Keyboard+Mouse+Joystick”*. When you select this device in the “*joy.cpl*” utility, click on the properties to display its preferences. The live values of the joystick axis and button activities will be displayed in a window similar to the one shown here: 

<p align="left" width="100%">
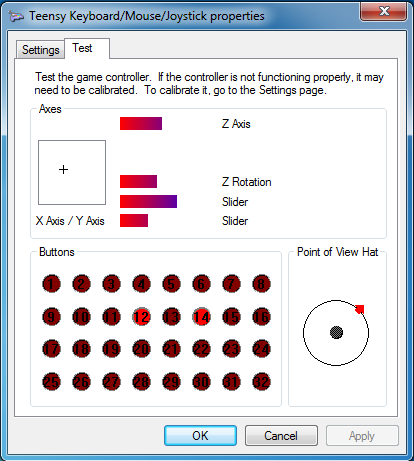
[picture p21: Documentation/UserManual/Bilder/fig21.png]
    
</p>

*Figure 19: Joy.cpl Properties*

Desired joystick button activities can be created using sip/puff or other interaction events by choosing “*Press Joystick Button*” from the action menu as described in the section [*Assignment of different actions*](https://github.com/asterics/FLipPad/blob/master/Documentation/UserManual/Markdown/FLipPadUserManual.md#assignment-of-different-actions-tab-actions).

### Sip/Puff Actions and Levels (Tab SIP AND PUFF) - OPTIONAL

If a pressure sensor is mounted (optional), it is possible to connect a tube this sensor, which outputs a value that corresponds to the detected pressure. When the user sips, the sensor value decreases, and when the user puffs, the value increases. 
You may assign actions for sipping or puffing using the tab “ACTIONS”, as will be explained in the next section. You can select the thresholds for sipping and puffing as desired, using the tab “SIP AND PUFF”. When the FLipPad is connected, you can also monitor the current pressure values and the triggering of sip/puff actions in this tab: 

<p align="left" width="100%">
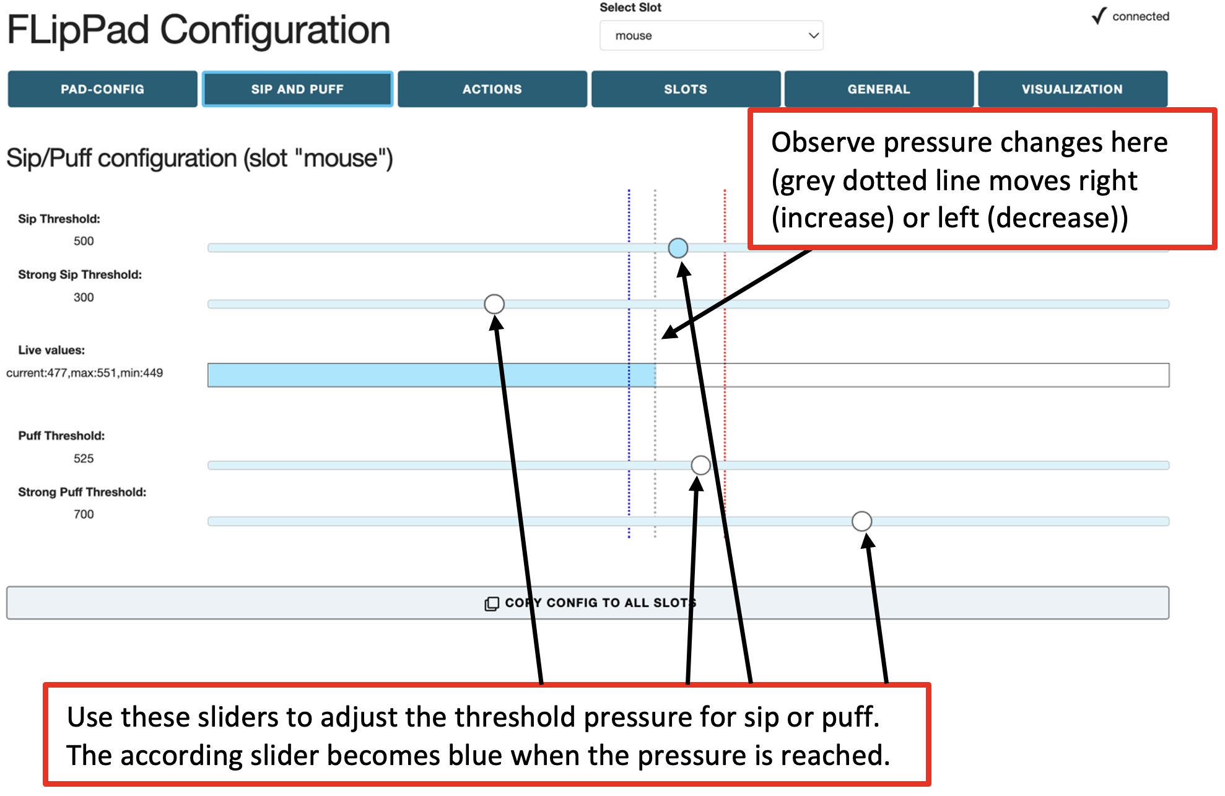
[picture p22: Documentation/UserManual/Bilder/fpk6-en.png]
    
</p>

*Figure 20: Tab SIP AND PUFF*

Note that the idle pressure level (without sip or puff) is 
around 512, and the level increases when you puff into the tube, indicating increased pressure.
With the sliders, the threshold pressure for sip and puff can be regulated. The grey dotted line represents the actual pressure. The blue and red dotted lines represent the limits reached in this session.

#### StrongSip and StrongPuff

The SIP AND PUFF tab allows to define additional threshold values for StrongSip or StrongPuff activities, which can then trigger distinct actions. For example, the next configuration slot could be activated by a strong puff. To enrich the functionality of the FLipPad especially for persons who cannot access external switches, additional StrongSip and StrongPuff gestures are available. These gestures allow to trigger actions via a strong sip or a strong puff followed by a stick movement (up / down / left / right).  A  strong sip or puff  is indicated via an acoustic signal (high tone). If the trackpad is touched and moved within one second, the corresponding action (for example “StrongSip+Up” is triggered). If the pad is not touched within one second, the single StrongSip or StrongPuff action will be triggered. Thus, a total of 10 additional actions can be performed.

### Assignment of different actions (Tab ACTIONS)

The ACTIONS tab allows the mapping of user activities to desired FLipPad functions (actions). The user activities are:

* pressing or releasing the 3 buttons (built-in button 1 or external button 2 or 3)
* pad gestures (tap, double tap, ...; tap + move into one direction)
* pad movements (up/down/left/right) which exceed the deadzone threshold value
* sip and puff activities (see section StrongSip and StrongPuff).

The actions can be changed via clicking the entry in the action configuration table (see the blue box in figure 21). The table shows the actions for all user activities, either only for the currently active slot, or for all slots (which gives an overview of all actions). When clicking one particular action,  a window pops up where you can change the action category (here for Button 1: Device) and the action itself (here: Load next slot), see Figure 22.

<p align="left" width="100%">
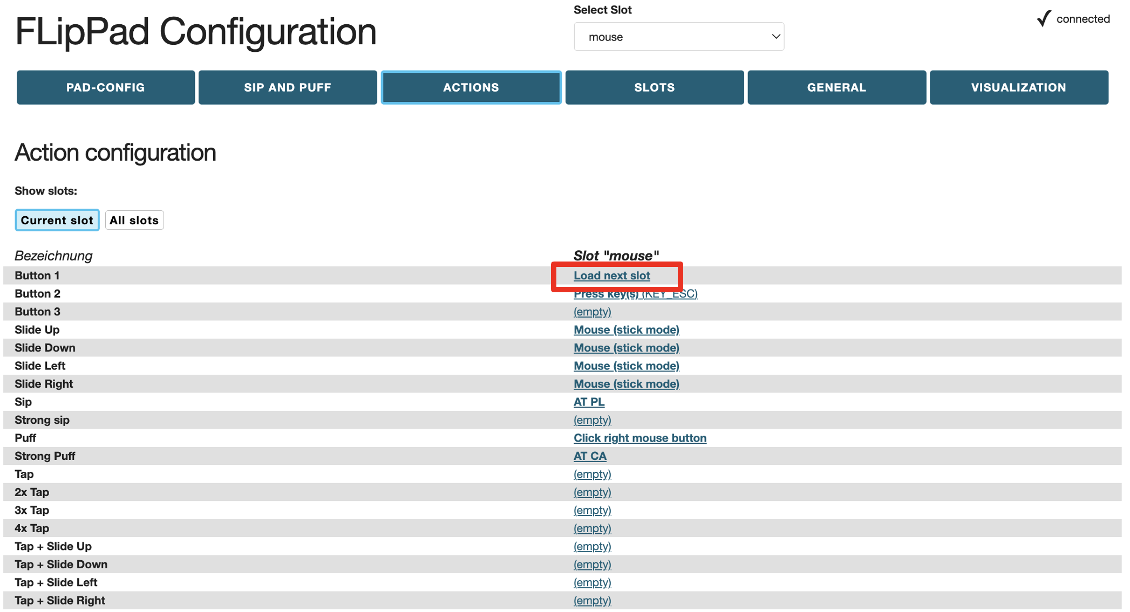
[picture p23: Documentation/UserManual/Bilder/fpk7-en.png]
    
</p>

*Figure 21: Assign different actions to user activities*

<p align="left" width="100%">
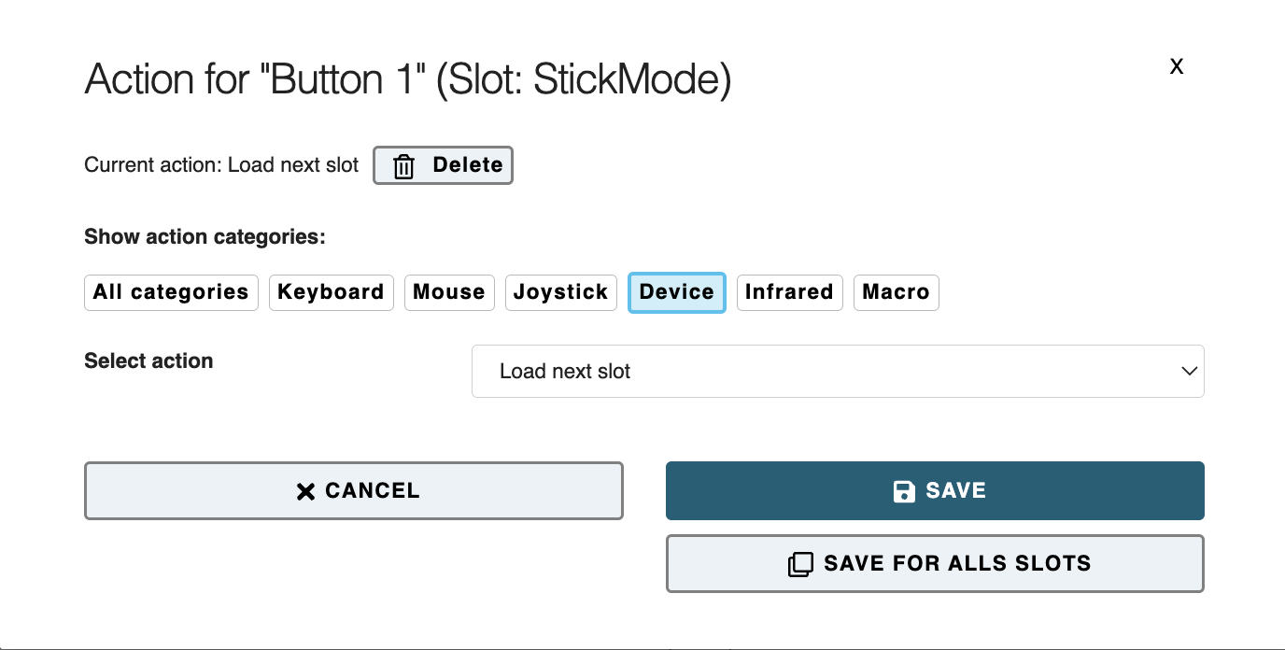
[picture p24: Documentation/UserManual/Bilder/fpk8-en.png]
    
</p>

*Figure 22: Pop-up window for choice of desired action*

In the following, the individual action categories and different actions will be briefly described.

#### Action category “Mouse”

**Hold Left / Middle / Right Mouse Button**
The *hold* action presses  a particular mouse button continuously (for example for dragging an item across the screen). The mouse button is released when the assigned user activity ends (for example when the sip/puff activity ends, when the pad is moved back to middle position or when an external button is released).

**Click Left / Middle / Right Mouse Button**
Creates mouse button clicks. (The left/right or middle mouse button is pressed and released again after a short time).

**Double Click Left Mouse Button**
Creates a double click with the left mouse button. 

**Toggle Left / Middle / Right Mouse Button**
The *toggle* action changes the state of a mouse button from pressed to not pressed and vice versa. This is useful e.g. if keeping a user activity up for a longer time (e.g. for dragging an item or for keeping a key pressed while other keys are pressed/released).

**Wheel Up / Down**
The actions *Wheel up* or *Wheel down* emulate the mouse scroll wheel. Triggering the *Wheel up* action results in upwards scrolling, while *wheel down* results in downward scrolling. This action is useful for example for reading documents or web sites.

**Move Mouse horizontally / vertically (x-axis / y-axis)**
The *Move mouse horizontally (x-axis)* and *Move mouse vertically (y-axis)* functions generate computer mouse movements along the selected axes. Speed parameters can be set for these functions in the field that appears below. As long as the user activity is present, the mouse pointer is accelerated up to this maximum speed. Please note that:

*A positive value for the X direction moves the mouse pointer to the right. 
A negative value for the X direction moves the mouse pointer to the left. 
A positive value for the Y direction moves the mouse pointer down. 
A negative value for the Y direction moves the mouse pointer up.*

#### Action category: Joystick

**Joystick set x-/y-/z-axis/slider**
These actions can be used to send a desired value to the joystick axis. The selectable joystick axes are: *X / Y / Z / Z-Turn / slider*. The joystick is moved back to middle position when the associated user activity ends.

**Press Joystick Button**
This action can be used to press a desired joystick button. The FLipPad device supports 32 buttons, so any value from 1 to 32 is allowed. The joystick button is released when the associated user activity ends.

**Joystick hat position**
This action sets the orientation of the joystick "hat" (in degrees). Allowed values are:
*-1, 0, 45, 90, 135, 180, 225, 270, 315*. The value of -1 sets the hat to the middle (idle) position. 
The joystick hat is moved back to middle position when the associated user activity ends. 

#### Action category: Keyboard

**Press / Hold / Toggle Keys**
The *Press Keys* action allows pressing one or multiple keyboard keys. A second drop-down menu with possible key identifiers is displayed (***Add keys***). **When a key is selected from this menu, it has to be added (Click ADD)** to the *Insert keys text* field. Thus, multiple keyboard keys can be pressed simultaneously. The keys are released when the associated user activity ends. If you would like to remove or change the assigned keys, you must clear the currently assigned keys by pressing the “CLEAR” button next to the Insert keys field. 

Common key combinations include: 
KEY_CTRL + Z: triggers undo function
KEY_CTRL + C: triggers copy function
KEY_CTRL + V: triggers paste function
KEY_CTRL + KEY_ALT + KEY_ DELETE

The *Hold Key* action keeps the key pressed until the user activity ends.
The *Toggle Key* action changes the key state from pressed to not pressed and vice versa with each user activity.

For a list of all supported key identifiers, see the [appendix](https://github.com/asterics/FLipPad/blob/master/Documentation/UserManual/Markdown/FLipPadUserManual.md#supported-key-identifiers).

<p align="left" width="100%">
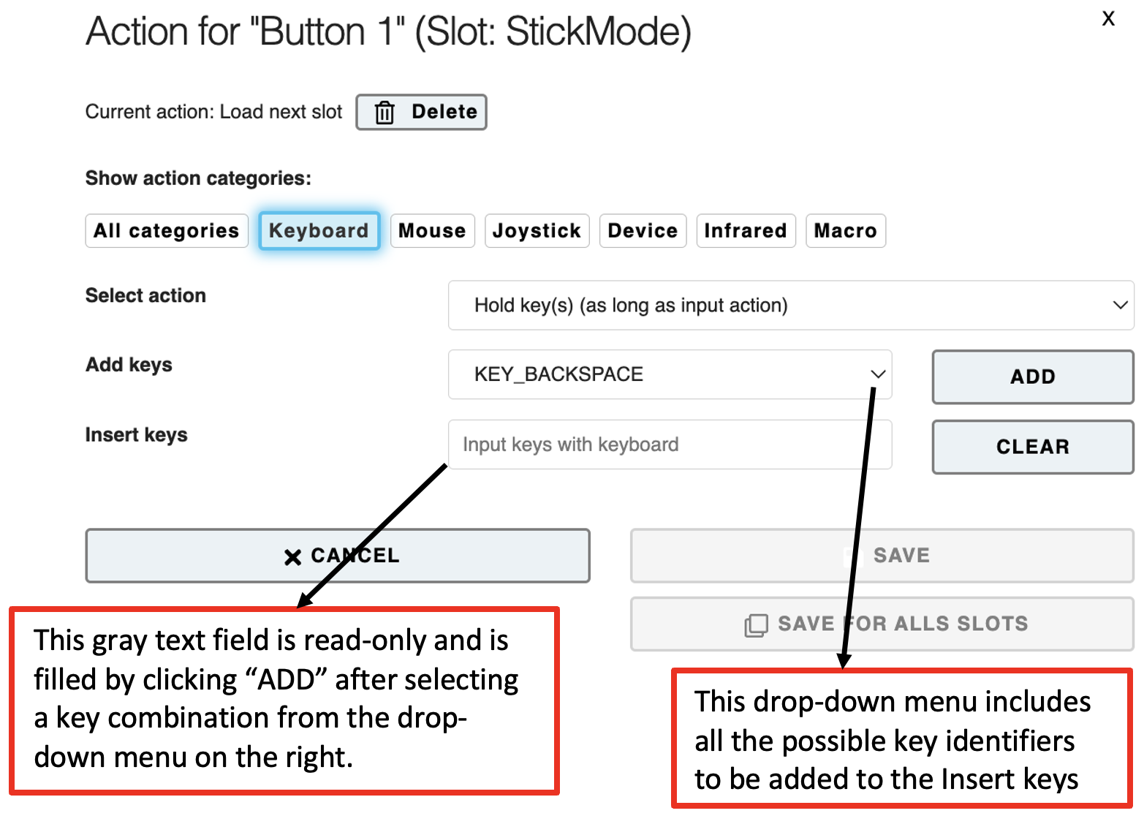
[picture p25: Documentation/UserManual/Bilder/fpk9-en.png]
    
</p>

*Figure 23: Add keys for the action press / hold / toggle keys*

**Write Word**
The *Write word* action allows typing a particular text/phrase whenever a user activity occurs (for example: write “Hello” whenever you tap the pad). Selecting this action displays a blank text box under the drop-down menu where the text can be entered, as shown below:

<p align="left" width="100%">
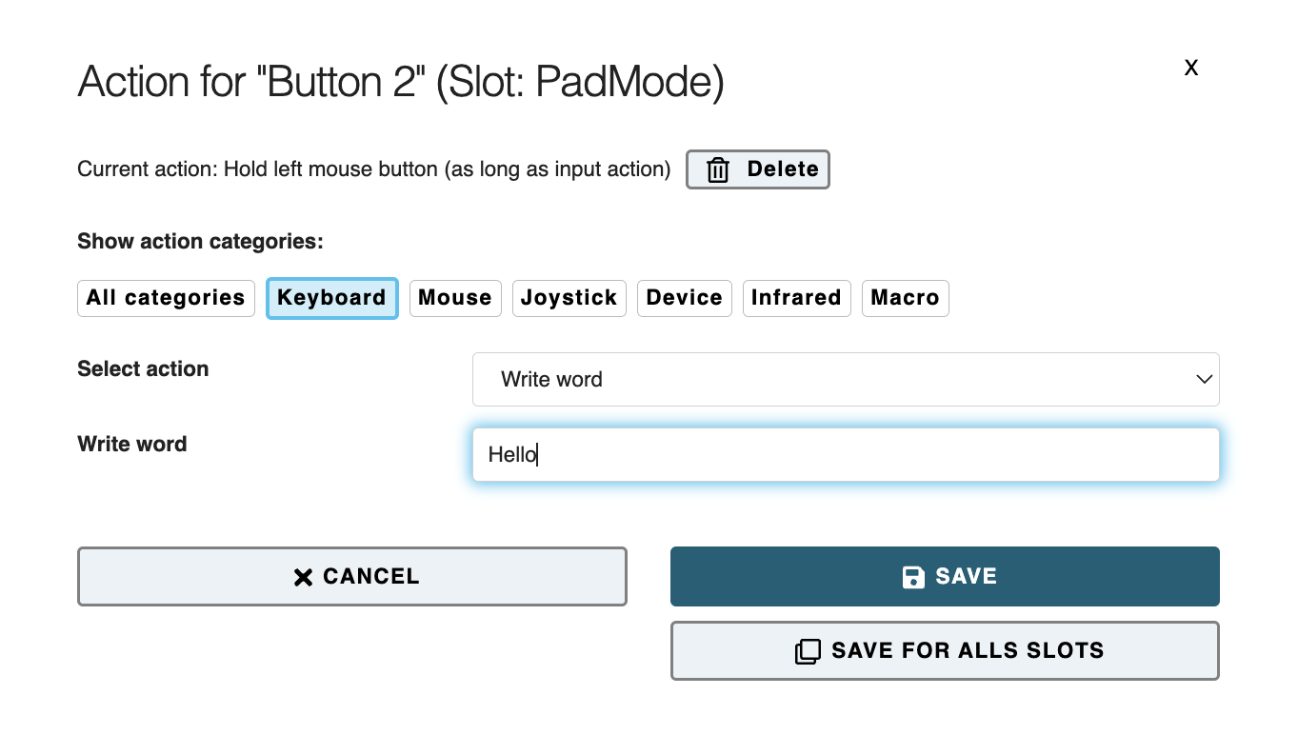
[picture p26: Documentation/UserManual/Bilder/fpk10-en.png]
    
</p>

*Figure 24: Write word function*

In this example, "Hello" will be written each time button 2 of the FLipPad is pressed.

#### Action category: Device

**No Command**
If the action *No Command* is selected, no action will be assigned to the respective user activity.

**Load Next Slot**
This action is only relevant if you have stored multiple FLipPad configuration slots. This action switches to the next slot. If the last slot is already reached, triggering this action will switch to the first slot.  When you switch the slot, the built-in LED bulbs will change accordingly, showing the active slot. 

There are three built in LEDs (red, yellow-orange, green), which will display the binary number for the slot position of the configuration that you have selected. In other words, if you saved two configurations, e.g. “Game settings” and “Mouse”, “Game settings” will be slot 1 and “Mouse” will be slot 2. 

Additionally to the LEDs, an acoustic signal will indicate the change of the slot.

The following list shows the color codes and the acoustic signals of the LEDs for each slot position:

| **Active Slot** | **Acoustic Signal** | **Shining LEDs**   |
| --------------- | ------------------- | ------------------ |
| Slot 1          | one beep tone       | red                |
| Slot 2          | two beep tones      | yellow             |
| Slot 3          | three beep tones    | red, yellow        |
| Slot 4          | four beep tones     | green              |
| Slot 5          | five beep tones     | red, green         |
| Slot 6          | six beep tones      | yellow, green      |
| Slot 7          | seven beep tones    | red, yellow, green |

The next figure (Figure 25) shows a similar list but the shining bulbs in the according colors for the visual people. The different slots are called "Position" in this figure.

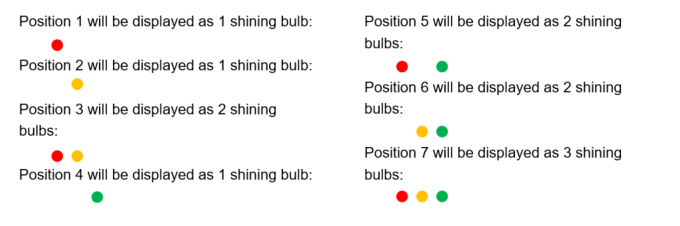
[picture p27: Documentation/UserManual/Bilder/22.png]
buttons


*Figure 25: Color codes of the LEDs*

**Load Slot by Name**
This action activates the configuration slot with the given name (if it exists). The name can be specified in the text field. This action is only relevant if you have stored multiple FLipPad configuration slots. The LEDs indicate the slot number as described above.

#### Action category: Infrared

**Play / Hold / Stop Infrared Command**
This action replays the infrared (IR-)code with the given command name. The existing (recorded) IR-commands can be selected from the drop-down menu. The *play* action sends the recorded code once, whereas the *hold* action repeats the code until the user activity ends. For more information about infrared codes please refer to section [“*Infrared Code Recording and Replay*”](https://github.com/asterics/FLipPad/blob/master/Documentation/UserManual/Markdown/FLipPadUserManual.md#infrared-code-recording-and-replay).

#### Action category: Macro

**Execute Command Macro**
This action allows running a so-called command macro which consists of several individual actions. Thus, a desired sequence of actions can be performed which consists for example of a number of mouse moves, mouse clicks, text inputs or key presses. This action is powerful, but also a bit more complicated because the individual actions must be specified in form of so-called AT-commands which are separated by semicolons. For example: the following command macro will move the mouse cursor 100 steps to the left, 20 steps up, then wait 100 milliseconds and then perform a left mouse click: “MX 100; MY -20; WA 100; CL”. For a list and detailed explanation of all supported AT-commands see [appendix](https://github.com/asterics/FLipPad/blob/master/Documentation/UserManual/Markdown/FLipPadUserManual.md#supported-macro-commands).

### Using Configuration Slots (Tab SLOTS)

In the SLOTS tab you can create new slots, delete existing slots, download a single or all slots and upload a file containing a complete configuration with multiple slots. After starting the FLipPad Configuration Manager, only one default slot named “mouse” exists. When you create a slot using the “CREATE SLOT” button, **the current slot is copied and appended** after the last existing slot. Before creating the new slot, assign a name in the corresponding field (“insert name for new slot”) that will help you remember the slot’s purpose:

<p align="left" width="100%">
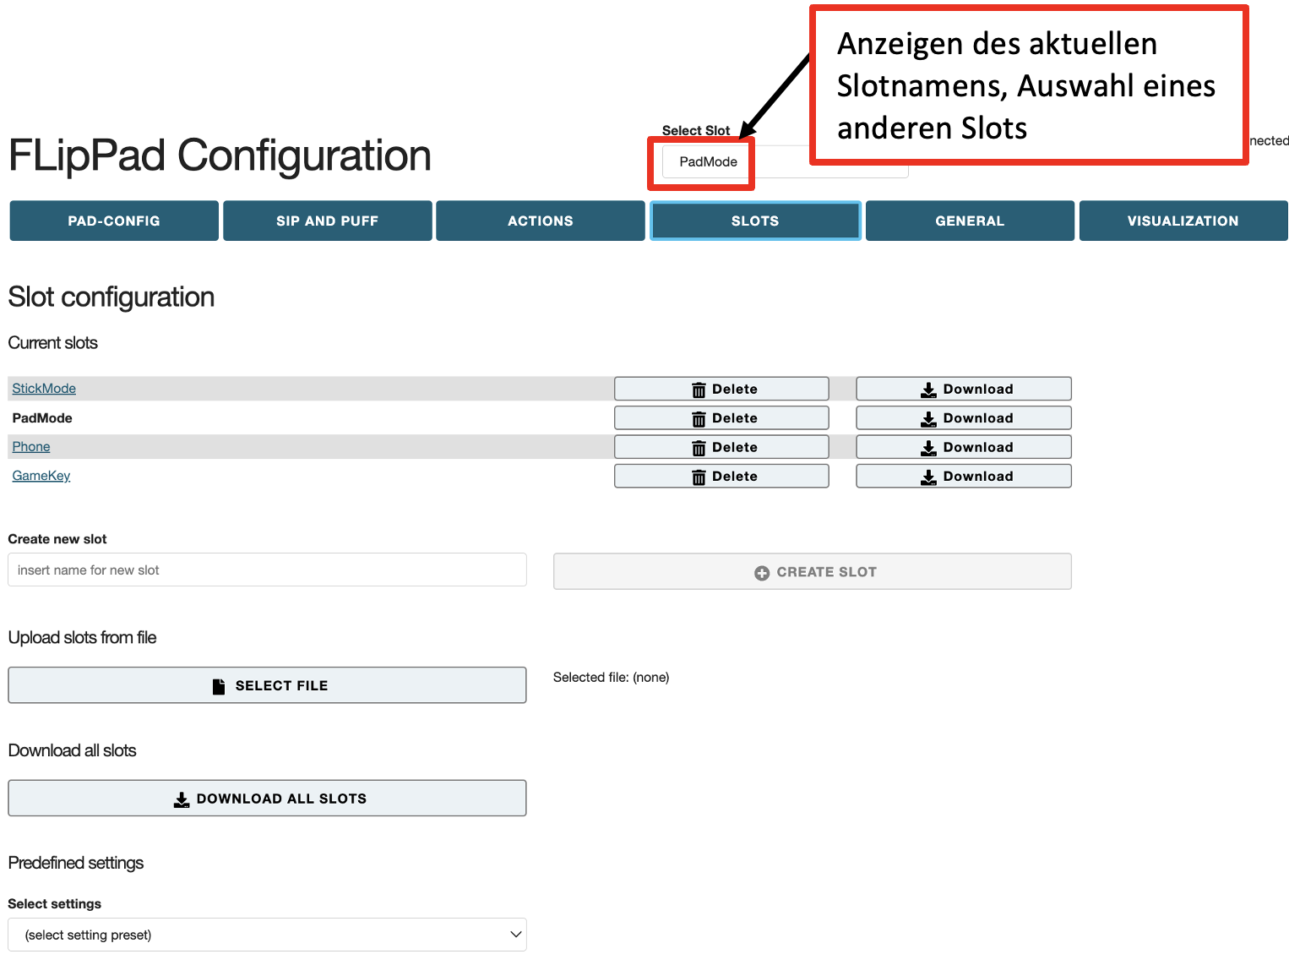
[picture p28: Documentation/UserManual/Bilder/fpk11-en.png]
    
</p>

*Figure 26: FLipPad Configuration Manager: Tab SLOTS*

At the top center of the Configuration Manager window (blue box in Figure 26) the current slot is shown and can be changed.
The settings of the current slot will be stored and remembered when changing to another slot. The maximum number of slots is 10. 

**Delete a slot**
A slot can be removed using the *Delete* button next to the according slot.

**Loading and saving the configuration to/from file**
The button *Download all slots* allows transferring all current slots to a setting file (.set) which is the stored on your computer. All settings can thus be transferred to the same or to another FLipPad device. Multiple setups (for example for individual users or use-cases) can be kept on a computer and applied with a single click. A file chooser window will be opened which allows selection of the desired filename for saving or loading the configuration.

### General Settings (Tab GENERAL)

The  GENERAL tab allows changing the USB/Bluetooth mode and apply firmware updates of the FLipPad device and the Bluetooth Add-On module (if installed):

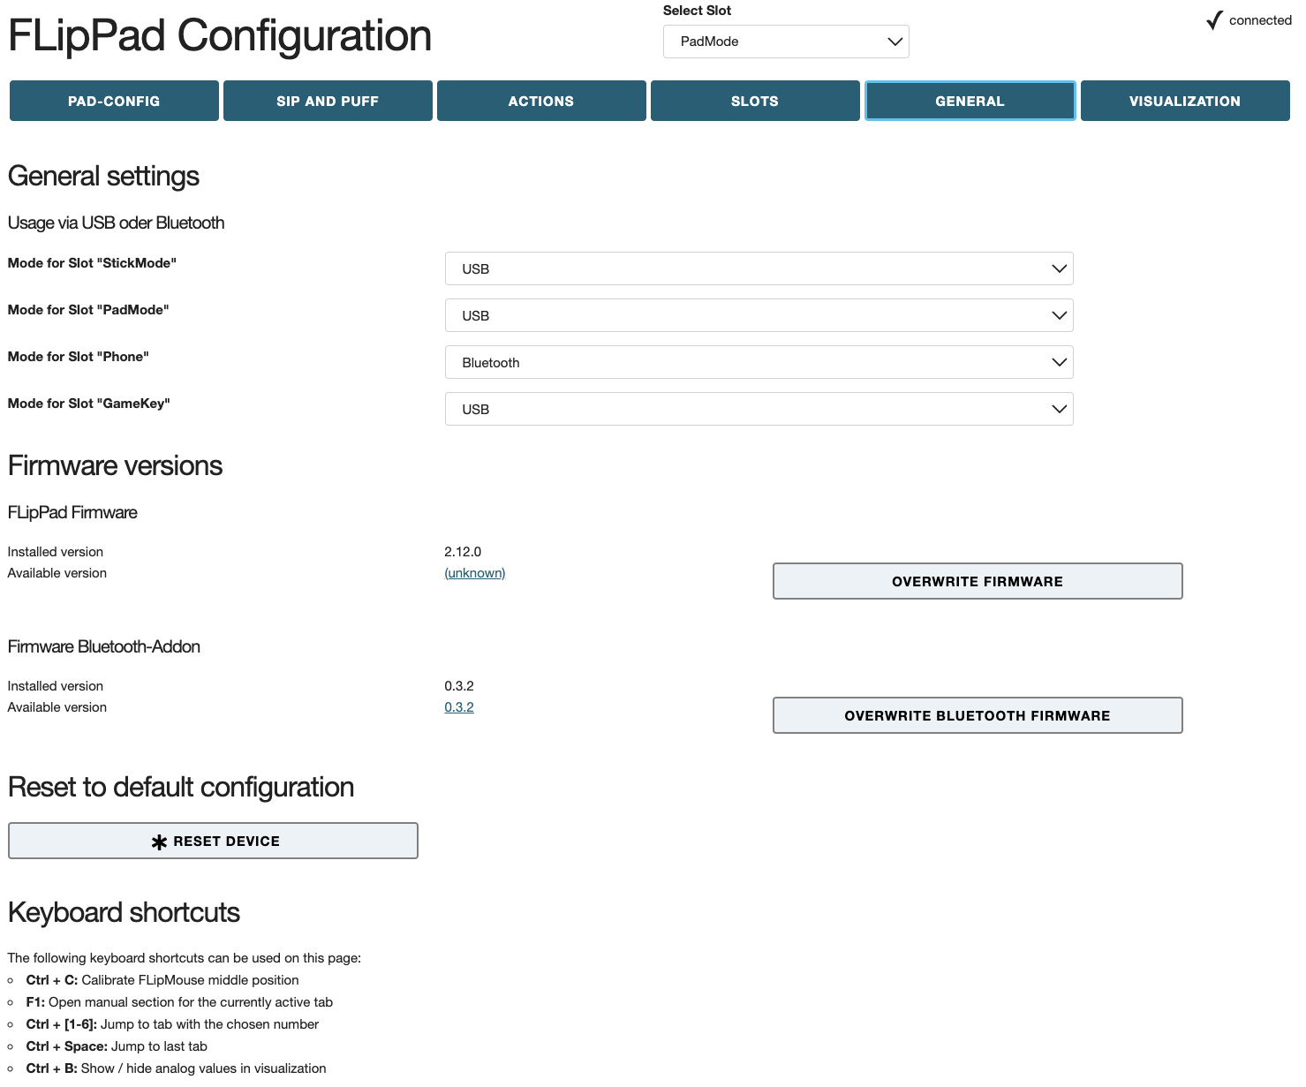
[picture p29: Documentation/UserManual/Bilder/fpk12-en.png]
general


*Figure 27: General Settings*

#### USB/Bluetooth mode 
This setting is only relevant if a Bluetooth Add-On module is attached (it is attached, if there is a version number for the Bluetooth-Addon on this page). Using this combo box selection, it is possible to decide if mouse / keyboard actions of a particular slot are sent via USB cable, via Bluetooth connection, or both. Thus, dedicated slots for USB and Bluetooth can be created, so that a user can switch e.g. from a laptop computer (where the FLipPad is connected via cable) to a wireless connection (phone / tablet) and back.

#### FLipPad Firmware (“UPDATE FIRMWARE”)

Here you can see the installed version and the available version of the FLipPad software (firmware). If the installed version is older than the version which is available online in the FLipPad Github repository, the button caption shows “UPDATE FIRMWARE”. Clicking the button will attempt to download the latest firmware and install it. If the installed version is newer or the same as the available version, the button caption shows “OVERWRITE FIRMWARE” - clicking the button will also download and install the version which is availbale online.

#### Firmware Bluetooth-Add-on (“UPDATE BLUETOOTH FIRMWARE”)

Here you can see the installed version and the available version of the Bluetooth Add-On moduleÄs firmware. Similar to the FLipPad firmware update you can click the button “UPDATE / OVERWRITE BLUETOOTH FIRMWARE”, which will attempt to download the latest software (firmware) for the Bluetooth module and install it on the module. This process can take a few minutes and is only possible if a Bluetooth module is connected to the FLipPad. If there is no Bluetooth module connected to the FLipPad, a message will indicate that the installed version is unknown. 

### View Force Levels (Tab VISUALIZATION)

The FLipPad stick is attached to four force sensors – one for each movement direction (up, down, left, right). The numeric value of each of those sensors is displayed in the “VISUALIZATION” tab. The live values can be monitored when the FLipPad device is connected. Whenever the pad is touche, the sensor values change. Specifically, a movement in each direction increases the respective value.

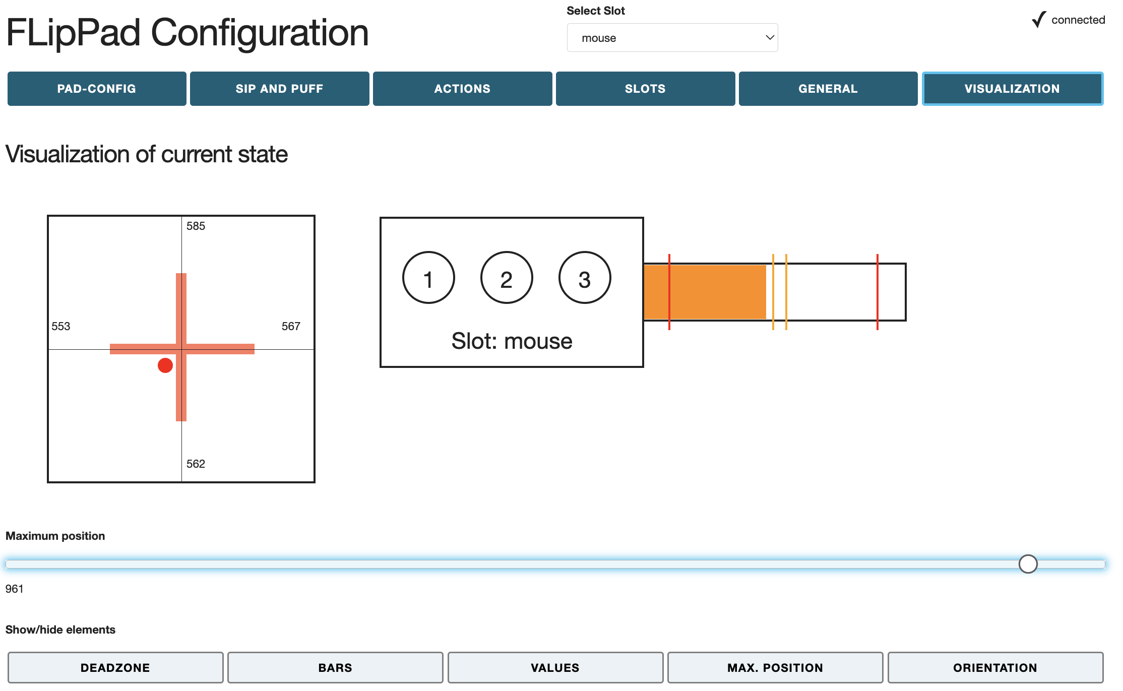
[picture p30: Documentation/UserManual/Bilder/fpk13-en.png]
visualisation


*Figure 28: Left: Live display of force sensor values; Middle: current slot with the 3 buttons (if one button is pressed, the corresponding circle will get yellow; Right: Sip and Puff live value and current thresholds*

### Infrared Code Recording and Replay

The FLipPad device includes an infrared remote control receiver module and a high current IR LED so that it can record and replay remote control codes of many remote control devices used in consumer electronics. If you want to use this feature of the FLipPad, make sure that the IR sending LED is points towards the device you want to control.

To record a new IR code, go to the tab ACTIONS. Click the desired action and select the action category “**Infrared**” in the popup-window. There, three different types of IR-actions can be selected from the combo box:

* *Play infrared command*: sends the recorded code once
* *Hold infrared command*: repeats the code until the user activity ends
* *Stop infrared command*: stops a currently plaing IR-code

The existing commands can be chosen from the drop-down menu.

In this window you can also manage IR commands. Next to *New IR Command*, you can enter a name and then click RECORD - point your IR remote to the side of the FLipPad where the LEDs stick out and send the IR command (there is a 10 seconds time limit for the recording phase). The new command is now stored in the FLipPad and can be chosen and replayed by selecting it's name in the drop down menu. If the command is not correctly replayed, try to increase the IR-Code timeout – for example to 250 milliseconds. Using *Delete IR command* commands can be deleted. 

<p align="left" width="100%">
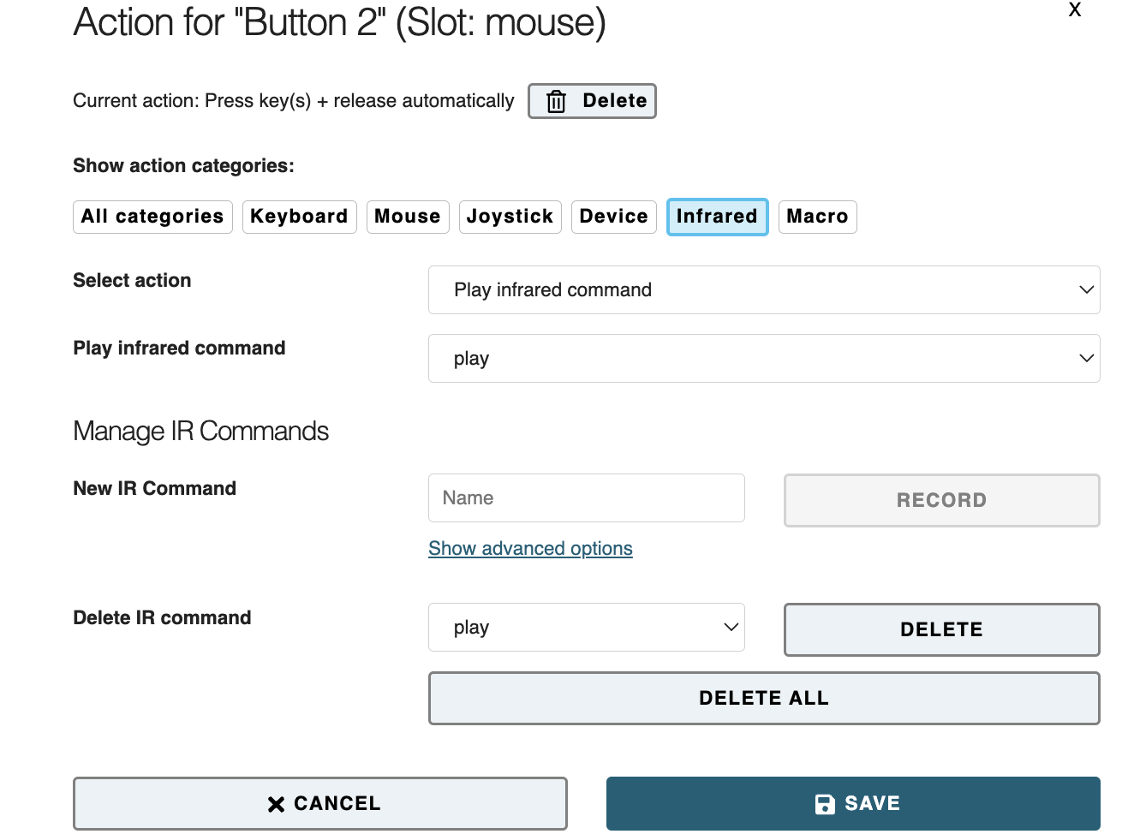
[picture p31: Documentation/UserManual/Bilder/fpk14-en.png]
    
</p>

*Figure 30: Infrared Recording and Replay Configuration Manager*

# Using the Bluetooth module

The optional Bluetooth Add-on module allows connection and control of cell phones, tablets and computers with Bluetooth capability. If the FLipPad is attached to a PC or laptop via USB, users may switch to Bluetooth operation and back to USB on demand. The Bluetooth module is available separately from the AsTeRICS Foundation or included in the appropriate version of the FLipPad kit. 

#### Installation of the Bluetooth module

The Bluetooth module is plugged onto the internal 10-pin connector of the FLipPad. To do this, open the FLipPad housing and push the module onto the pin header as far as possible:

<p align="left" width="100%">
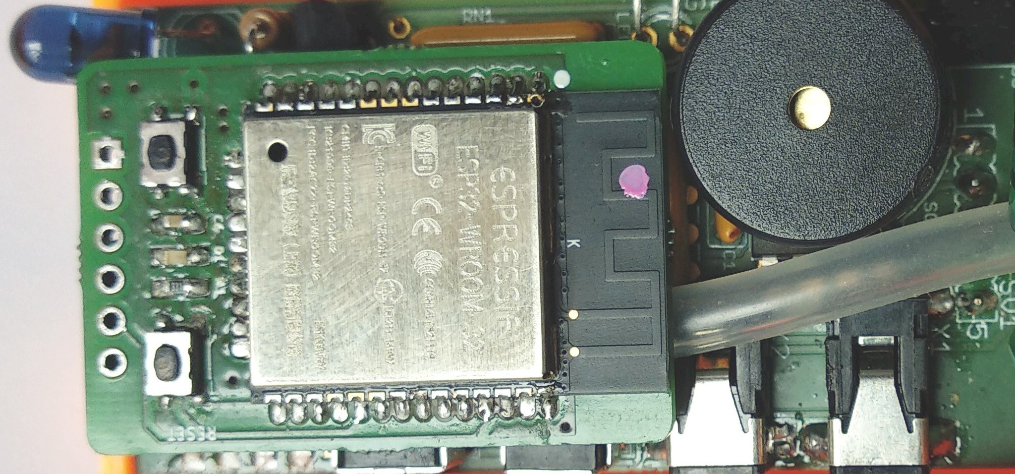
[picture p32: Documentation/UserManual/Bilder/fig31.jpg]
    
</p>

*Figure 31: Bluetooth module*

#### Connecting with a Bluetooth host device (pairing)

The host device could be a cell phone with Android or iOS operating system, for example. 
The FLipPad can be connected to a host device only if no device is currently connected, and thus pairing mode is active. In order to connect a device, open the Bluetooth settings of your Android or iOS device, enable BT, choose *add a new BT-device* and select the FLipPad from the list of availabe devices.  Then, open the GENERAL tab and activate Bluetooth operation for the desired slots (see section [*General Settings*](https://github.com/asterics/FLipPad/blob/master/Documentation/UserManual/Markdown/FLipPadUserManual.md#general-settings-tab-general)).

Note:  If the Bluetooth module is in paring mode, the module's LED flashed fast (approx twice per second). If a connection is established, the LED flashes slowly (approx. once every 2 seconds). The LED can only be seen if the enclosure of the FLipPad is opened.

# Updating the Firmware via Arduino IDE

In addition to the possibility of updating the FLipPad firmware via the configuration manager, the firmware can also be updated via the Arduino IDE and the Teensyduino add-on / loader application. Find the most recent versions in the latest release package on [Github](https://github.com/asterics/FLipPad/releases). Unzip the FLipPad.zip package and start the teensy.exe program (the Teensy Loader).

<p align="left" width="100%">
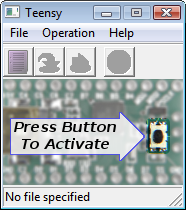
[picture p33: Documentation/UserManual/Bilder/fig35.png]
    
</p>

*Figure 34: Teensy Loader Step 1*

The Teensy Loader user interface should look as on the picture above (Figure 34). If there is any security warning (related to Windows User Access Control), please ensure that the Publisher is “PJRC.COM, LLC” and click on “Run”.
As next step, activate the “download mode” of the FLipPad by using some pointed tool (needle, small screwdriver, …) to press the reset button which is accessible via the small hole on the bottom side. After a few seconds (driver installation), the Teensy Loader GUI should indicate connection to the FLipPad as shown here in the following Figure:

<p align="left" width="100%">
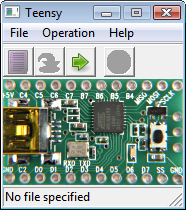
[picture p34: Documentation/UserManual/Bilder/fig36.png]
    
</p>

*Figure 35: Teensy Loader Step 2*

Choose “File → Open HEX file” and select the file “FLipWare.hex” from the FLipPad folder (or location where you downloaded the release .zip file).

Select “Operation → Program”. After a few seconds, you should see the notification “Download complete”, as on the next picture (Figure 36). (If this step does not work in the first place, try to unplug and replug the FLipPad and restart the Teensy Loader software.)

<p align="left" width="100%">
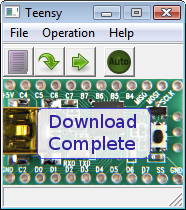
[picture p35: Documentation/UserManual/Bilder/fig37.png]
    
</p>

*Figure 36: Teensy Loader Step 3*

To finish the firmware installation, select “Operation → Reboot”.
You should read “Reboot” and the FLipPad should beep for a short time.

<p align="left" width="100%">
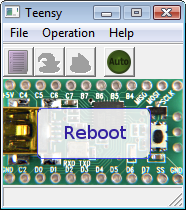
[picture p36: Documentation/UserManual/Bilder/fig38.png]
    
</p>

*Figure 37: Teensy Loader Step 4*

To update the GUI software, copy the file “FLipPadGUI.exe” from the zip package to the desired location (replacing the old FLipPadGUI.exe file).

# Building the Firmware

If you want to adapt the software (firmware) of the FLipPad, please have a look at the README file of our repository: https://github.com/asterics/FLipPad 

# Further instructions and troubleshooting

For further instruction and troubleshooting please contact us: office@asterics-foundation.org

# Appendix: Macro commands and Key codes

## Supported Macro commands:

| **Abbreviation** | **Function**                                                                                                                   | **example**                                                                                                                     |
| ---------------- | ------------------------------------------------------------------------------------------------------------------------------ | ------------------------------------------------------------------------------------------------------------------------------- |
| CL               | click left mouse button                                                                                                        |                                                                                                                                 |
| CR               | click right mouse button                                                                                                       |                                                                                                                                 |
| CM               | click middle mouse button                                                                                                      |                                                                                                                                 |
| CD               | click double with left mouse button                                                                                            |                                                                                                                                 |
| HL               | hold the left mouse button                                                                                                     |                                                                                                                                 |
| HR               | hold the right mouse button                                                                                                    |                                                                                                                                 |
| HM               | hold the middle mouse button                                                                                                   |                                                                                                                                 |
| TL               | toggle left mouse button                                                                                                       | changes the state of the mouse button                                                                                           |
| TM               | toggle middle mouse button                                                                                                     |                                                                                                                                 |
| TR               | toggle right mouse button                                                                                                      |                                                                                                                                 |
| RL               | release the left mouse button                                                                                                  |                                                                                                                                 |
| RR               | release the right mouse button                                                                                                 |                                                                                                                                 |
| RM               | release the middle mouse button                                                                                                |                                                                                                                                 |
| WU               | move mouse wheel up                                                                                                            |                                                                                                                                 |
| WD               | move mouse wheel down                                                                                                          |                                                                                                                                 |
| MX <int>         | move mouse in x direction                                                                                                      | MX 4 -> moves cursor 4 pixels to the right                                                                                      |
| MY <int>         | move mouse in y direction                                                                                                      | MY -10 -> moves cursor 10 pixels up                                                                                             |
| RO <int>         | rotate stick orientation                                                                                                       | RO 180 -> flips x and y movements of stick/mouthpiece                                                                           |
| KW <string>      | keyboard write string                                                                                                          | KW Hello! -> writes "Hello!" on the keyboard                                                                                    |
| KP <string>      | key press: Press keyboard keys (once). Keys are identified by keyboard shortcuts (see list below)                              | KP KEY_UP -> presses the "Cursor-Up" key; KP KEY_CTRL KEY_ALT KEY_DELETE presses all 3 keys                                     |
| KH <string>      | key hold: hold keyboard keys                                                                                                   | sKH KEY_LEFT -> holds the "Cursor-Left" key                                                                                     |
| KT <string>      | key toggle: toggle keyboard keys; the key will remain pressed until "AT KT" command is sent again or a "AT KR" command is sent | KT KEY_DOWN -> toggles the "Cursor-Down" key                                                                                    |
| KR <string>      | key release                                                                                                                    | KR KEY_UP -> releases the "Cursor-Up" key                                                                                       |
| RA               | releases all = Release all currently pressed keys and mouse buttons                                                            |                                                                                                                                 |
| WA <int>         | wait a certain number of milliseconds                                                                                          | WA 100 -> waits 100 milliseconds                                                                                                |
| NE               | next slot: load next slot                                                                                                      |                                                                                                                                 |
| LO <string>      | Load slot per name, changes to the given slot                                                                                  | LO mouse                                                                                                                        |
| NC               | No command                                                                                                                     |                                                                                                                                 |
| JX <int>         | set joystick x axis                                                                                                            | JX 512 -> sets the x-axis to middle position                                                                                    |
| JY <int>         | set joystick y axis                                                                                                            | JY 1023 -> sets the y-axis to full up position                                                                                  |
| JZ <int>         | set joystick z axis                                                                                                            | JZ 0 -> sets the z-axis to lowest poistion                                                                                      |
| JT <int>         | set joystick turn axis                                                                                                         | JT 512 -> sets the rotation to middle position                                                                                  |
| JS <int>         | set joystick slider position                                                                                                   | JS 512 -> sets the slider to middle position                                                                                    |
| JP <int>         | press joystick button                                                                                                          | JP 1 -> presses joystick button 1                                                                                               |
| JR <int>         | release joystick button                                                                                                        | JR 2 -> releases joystick button 2                                                                                              |
| JH <int>         | set joystick hat position                                                                                                      | JH 45 -> sets joystick hat to 45 degrees; possible values are: 0, 45, 90, 135, 180, 225, 270, 315 and -1 to set center position |
| MM <int>         | mouse mode: cursor on (int=1) or alternative functions on (int=0)                                                              | MM1 -> switches to mouse mode                                                                                                   |
| CA               | Calibrate zero position                                                                                                        | calibrates stick / mouthpiece middle position                                                                                   |
| IP <string>      | play infrared command                                                                                                          | IP channelUp; plays infrared command "channelUp" (if this IR-command name has been recorded)                                    |

Please note that certain commands for adjusting FLipPad settings are not shown in this table (for example setting thresholds or accelerations, recording IR-commands etc.). For a full list of commands please refer to the [FLipPad wiki](https://github.com/asterics/FLipPad/wiki/at-api). 

## Supported Key Identifiers:

| **Supported KEY Identifiers:**                                                                                                                                                                                                                                                                     |
| -------------------------------------------------------------------------------------------------------------------------------------------------------------------------------------------------------------------------------------------------------------------------------------------------- |
| **Letters**                                                                                                                                                                                                                                                                                        |
| KEY_A  KEY_B  KEY_C  KEY_D  KEY_E  KEY_F  KEY_G  KEY_H  <br/>KEY_I  KEY_J  KEY_K  KEY_L  KEY_M  KEY_N  KEY_O  KEY_P  <br/>KEY_Q  KEY_R  KEY_S  KEY_T  KEY_U  KEY_V  KEY_W  KEY_X                                                                                                                   |
| **Digits**                                                                                                                                                                                                                                                                                         |
| KEY_1  KEY_2  KEY_3  KEY_4  KEY_5  KEY_6  KEY_7  KEY_8  KEY_9  KEY_0                                                                                                                                                                                                                               |
| **Function keys**                                                                                                                                                                                                                                                                                  |
| KEY_F1  KEY_F2  KEY_F3  KEY_F4  KEY_F5  KEY_F6  KEY_F7  KEY_F8  KEY_F9  KEY_F10  <br/>KEY_F11  KEY_F12  KEY_F13  KEY_F14  KEY_F15  KEY_F16  KEY_F17  KEY_F18  KEY_F19 <br/>KEY_F20  KEY_F21  KEY_F22  KEY_F23  KEY_F24                                                                             |
| **Navigation keys**                                                                                                                                                                                                                                                                                |
| KEY_UP  KEY_DOWN  KEY_LEFT  KEY_RIGHT  KEY_TAB  KEY_PAGE_UP  KEY_PAGE_DOWN <br/>KEY_HOME  KEY_END                                                                                                                                                                                                  |
| **Special keys**                                                                                                                                                                                                                                                                                   |
| KEY_ENTER  KEY_SPACE  KEY_BACKSPACE  KEY_DELETE  KEY_INSERT  KEY_ESC  KEY_NUM_LOCK<br/>KEY_SCROLL_LOCK  KEY_CAPS_LOCK  KEY_PAUSE<br/><br/>KEY_SEMICOLON  KEY_COMMA  KEY_PERIOD  KEY_MINUS  KEY_EQUAL  KEY_SLASH<br/>KEY_BACKSLASH  KEY_LEFT_BRACE  KEY_RIGHT_BRACE  KEY_QUOTE  KEY_TILDE  KEY_MENU |
| **Keypad keys**                                                                                                                                                                                                                                                                                    |
| KEYPAD_1  KEYPAD_2  KEYPAD_3  KEYPAD_4  KEYPAD_5  KEYPAD_6  KEYPAD_7  KEYPAD_8<br/>KEYPAD_9  KEYPAD_0  <br/>KEYPAD_SLASH  KEYPAD_ASTERIX  KEYPAD_MINUS  KEYPAD_PLUS  KEYPAD_ENTER  KEYPAD_PERIOD                                                                                                   |
| **Keys for alternative functions**                                                                                                                                                                                                                                                                 |
| KEY_SHIFT  KEY_CTRL  KEY_ALT  KEY_RIGHT_ALT  KEY_GUI  KEY_RIGHT_GUI                                                                                                                                                                                                                                |

# Contact Information

University of Applied Sciences Technikum Wien

Faculty of Electronic Engineering

Höchstädtplatz 6

A-1200 Wien

AUSTRIA

AsTeRICS Foundation

Webpage: [www.asterics-foundation.org](http://www.asterics-foundation.org)

Email: <office@asterics-foundation.org>

# Disclaimer

The University of Applied Sciences Technikum Wien and the AsTeRICS Foundation do not assume any warranty and liability for the functionality of the described devices, software and the correctness of the documents handed over.

Additionally, the UAS TW is not liable for any damages to health due to the use of described hardware or software. The provided software applications and hardware modules are to be used at own risk!

# Acknowledgement

This project was partly funded by the City of Vienna, 
Municipal department of Economic Affairs, Labor and Statistics (MA 23), 
in course of the projects AsTeRICS Academy (14-02), ToRaDes (18-04) 
and Wissensdrehscheibe für Barrierefreie Technologien (26-02) 

Logos

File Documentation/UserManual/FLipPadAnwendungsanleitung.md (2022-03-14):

# FlipPad - Finger Trackpad

**Anwendungsanleitung v3.1, AsTeRICS Foundation**

FLipPadLogo

**Inhaltsverzeichnis:**

[TOC]

__Achtung: erster Entwurf!__

---

# Einleitung

Das FLipPad ist ein alternatives Eingabesystem, das an der [Fachhochschule Technikum Wien](https://www.technikum-wien.at) entwickelt und von der [AsTeRICS Foundation](https://asterics-foundation.org) als Open Source Baukasten angeboten wird. Das FLipPad ermöglicht es Menschen, die keine Standard-Computer-Eingabegeräte verwenden können, eine Computermaus oder einen Joystick zu steuern, sowie die gewünschten Tasten auf der Tastatur zu drücken oder Infrarot-Fernbedienungen zu verwenden. Das FlipPad kann mit minimalen Fingerbewegungen und Gesten betätigt werden.

Das FlipPad kann über eine webbasierte Konfigurationsanwendung konfiguriert werden, die von nun an *Konfigurationsmanager* genannt wird. Sie ist auf der Website [FlipPad.asterics.eu](https://flippad.asterics.eu) zu finden. Dieses Benutzerhandbuch enthält eine Beschreibung des Konfigurationsmanagers und erklärt, wie die verschiedenen Funktionen und Merkmale des FlipPad verwendet werden. Das FlipPad kann auf jedem Windows-, Mac- oder Linux-Computer ohne Installation von spezieller Software verwendet werden, da es sich wie ein Standard-Maus/Joystick/Tastatur-Gerät verhält. Mit dem optionalen Bluetooth-Zusatzmodul können auch Smartphones oder Tablet-Computer angesteuert werden - was ebenfalls in diesem Handbuch erklärt wird.

Darüber hinaus enthält dieses Handbuch wichtige Richtlinien für die Verwendung des FlipPad.

Alle Designdateien für die Elektronik und das 3d-gedruckte Gehäuse - sowie der Software-Quellcode - sind Open Source verfügbar und werden über die Website der AsTeRICS Foundation und über GitHub verbreitet. Der Bausatz für des FlipPad kann bei [Hackerspaceshop.com](https://hackerspaceshop.com/collections/FlipPad) (Seite muss erst erstellt werden)erworben werden. Detaillierte Anleitungen sind in der [FlipPad-Bauanleitung](https://github.com/asterics/FlipPad/blob/master/ConstructionKit/ConstructionManual.pdf) enthalten. Viel Spaß beim Bauen und Benutzen deines FlipPads!

Die AsTeRICS Foundation

[www.asterics-foundation.org](https://asterics-foundation.org/)

<p align="center" width="100%"> Flip, the vagabound grasshopper cartoon character </p>

# Hardware Übersicht

Das FlipPad ist mit einem 3d-gedruckten Gehäuse erhältlich. Designdateien für das 3d-gedruckte Gehäuse werden im [Github-Repository](https://github.com/asterics/FLipPad/tree/main/Hardware/case-design/smallTrackpad_TM035035) bereitgestellt. In weiterer Folge wird eine FlipPad mit einem größeren Touchbett entwickelt. 



*Abbildung 1*: Verwendung des FlipPad für die Computersteuerung durch Fingerinteraktion

Zusätzlich können zwei externe Taster an die Klinkenbuchsen auf der linken Seite des FlipPad-Gehäuses angeschlossen werden und eine Taste ist bereits auf dem Gerät integriert ("B1", siehe Abbildung 3).

**Benutzer können auf verschiedene Weise mit dem FlipPad interagieren:**

1. durch Berühren des Touchpads mit den Fingern und Aufbringen kleiner, bis gar keiner Kräfte in vertikaler oder horizontaler Richtung
2. durch Erhöhen oder Verringern des Drucks 
3. durch Betätigung von (bis zu) 3 Schaltern / Drucktastern

**Die Hardware-Eigenschaften des FlipPad:** (siehe Bilder am Ende dieser Liste)

(a)    Ein eingebauter Schalter ("Taste 1 / B1") am Gerät, z.B. zum Ändern der aktiven Konfiguration (Funktionen)

(b)    Zwei 3,5-mm-Klinkenbuchsen zum Anschluss von externen Schaltern / Tastern zur Auslösung von Zusatzfunktionen ("Taster 2 / B2" und "Taster 3 / B3")

(c)    3 Leuchtdioden (LED) zur Anzeige der aktiven Konfiguration, des Kalibrierungsvorgangs usw.

(d)    Universal-Infrarot-Fernbedienungsempfänger und -sender

(e)    "Hot Shoe"-Adapter zur Montage an einem Manfrotto Magic Arm oder einem ähnlichen Montagesystem

(f)    Firmware-Aktualisierung über die FlipPad-Webanwendung auf [FlipPad.asterics.eu](https://flippad.asterics.eu/index_pad.htm)

(g)    Optionale Zusatzplatine für Bluetooth (z. B. zur Steuerung von Smartphones oder iOS-Geräten)

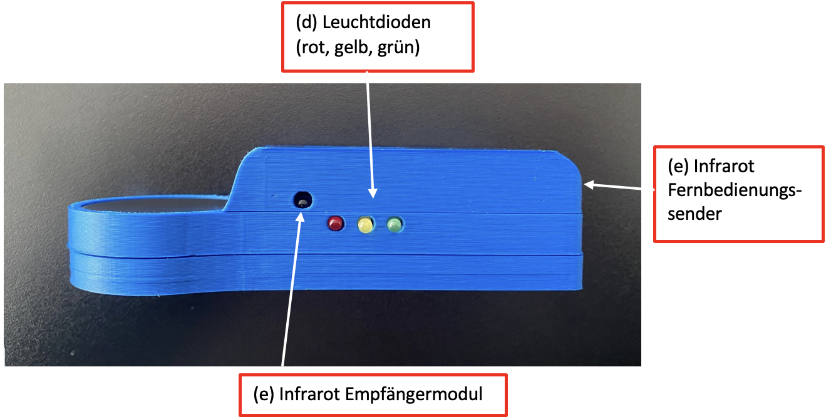
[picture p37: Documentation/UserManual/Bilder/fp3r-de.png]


*Abbildung 2*: FlipPad rechte Seite

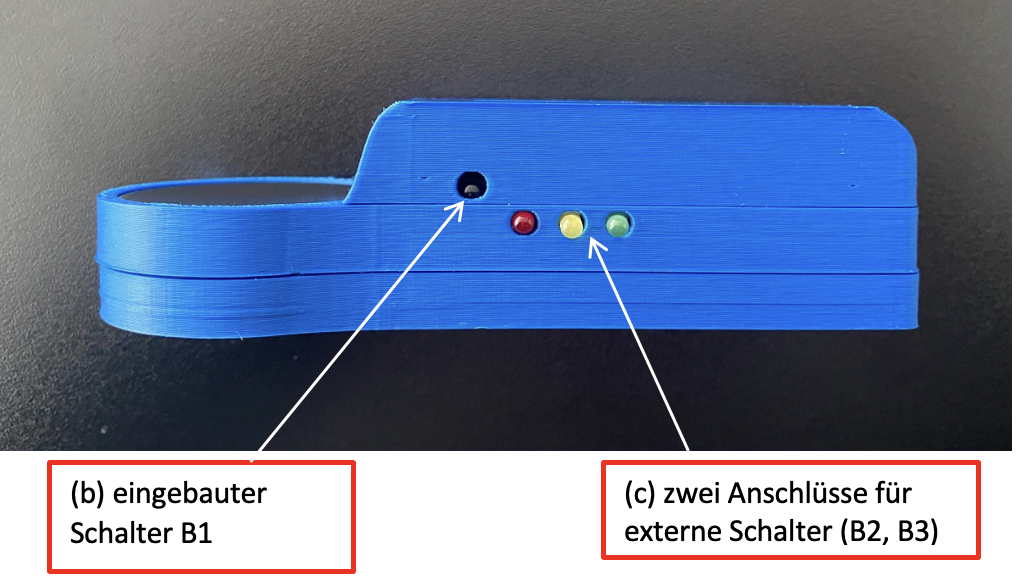
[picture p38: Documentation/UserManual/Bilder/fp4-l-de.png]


*Abbildung 3*: FlipPad linke Seite

Auf der rechten Seite des FlipPad-Gehäuses zeigen 3 LEDs den aktuellen Betriebsmodus an (der geändert werden kann, um verschiedene Geschwindigkeitseinstellungen oder Funktionsoptionen zu aktivieren). Außerdem ist hier das Infrarot (IR) Empfängermodul zugänglich. Mit diesem Modul können beliebige Infrarot-Fernbedienungsbefehle aufgezeichnet werden (z.B. zum Ändern der Lautstärke oder der Kanaleinstellungen eines TV-Gerätes). Die IR-Signale können dann über die IR-Sendediode auf der Rückseite des FlipPad wiedergegeben werden.

Auf der linken Seite des FlipPad befindet sich eine Taste (B1), die eine konfigurierbare Funktion bietet (z. B. Ändern des Betriebsmodus). Zwei 3,5-mm-Klinkenbuchsen mit den Bildbezeichnungen (B2) und (B3) ermöglichen den Anschluss von externen Tastern. Es können Standardschalter mit 3,5-mm-Klinkenstecker verwendet werden.

## 3D-gedrucktes Gehäuse

<p align="left" width="100%">
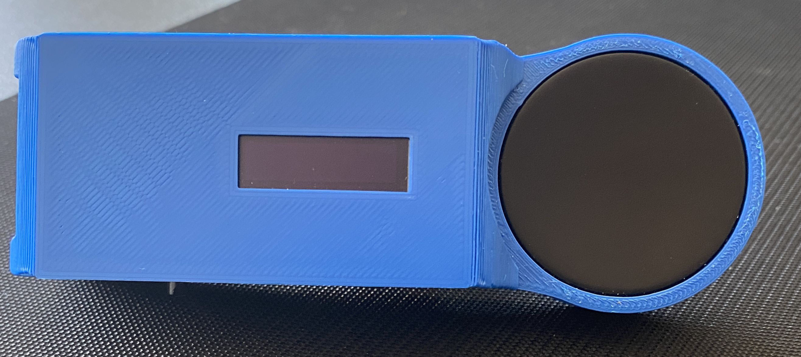
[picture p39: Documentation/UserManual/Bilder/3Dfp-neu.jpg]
    
</p>
*Abbildung 4*: FlipPad 3D-gedrucktes Gehäuse 

Es sind verschiedene Alternativen für das FlipPad-Gehäuse verfügbar, z.B. eine Acrylversion. Die empfohlene Version ist das 3D-gedruckte Gehäuse, das auch in der Bauanleitung dokumentiert ist. Die 3D-Designdateien können vom [Github Repository](https://github.com/asterics/FLipPad/tree/main/Hardware) heruntergeladen werden. 

## Bluetooth – Zusatzmodul

Das optionale Bluetooth-Zusatzmodul ermöglicht den Anschluss des FlipPad als Bluetoothmaus/ -tastatur an verschiedene mobile Geräte (Smartphones, Tablets, IOs-Geräte). Wenn dieses Modul nicht im DIY-Kit enthalten ist, kann es einzeln bei der AsTeRICS Foundation bestellt oder mit Hilfe der auf Github verfügbaren Hardware-Design-Dateien gebaut werden (Teile müssen einzeln bestellt werden). Wenn Sie sich für diese Funktion interessieren, werfen Sie einen Blick auf das [FlipPad Wiki](https://github.com/asterics/FlipPad/wiki), wo der Bau des Zusatzmoduls erklärt wird. 



*Abbildung 5*: Bluetooth Zusatzmodul

# Anweisungen für die ordnungsgemäße Montage und Verwendung

**1. Montieren des FlipPad-Geräts in einer für den Benutzer / die Benutzerin geeigneten Weise** 


*Abbildung 7*: Montieren des FlipPad

Das Bild zeigt eine Kombination aus "[Manfrotto Gelenkarm](https://www.manfrotto.com/global/single-arm-2-section-196ab-2/)" + "[SuperClamp](https://www.manfrotto.com/global/super-photo-clamp-without-stud-aluminium-035/)" Halterung. Sie können auch den [Manfrotto Magic Arm](https://www.manfrotto.com/global/magic-photo-arm-smart-centre-lever-and-flexible-extension-143n/) oder eine andere Befestigungslösung verwenden, die auf den HotShoe-Adapter der FlipPad passt. Seien Sie vorsichtig, wenn Sie die Halterung an der 3/8"-Schraube des HotShoe-Adapters befestigen: Bei starker Krafteinwirkung kann das Gehäuse des Geräts brechen.



*Abbildung 9*: Verwendung der FlipPad mit den Fingern

Wenn der Benutzer / die Benutzerin das FlipPad mit einem Finger oder dem Daumen betätigen möchte, montieren Sie das System so, dass sich die Hand in einer Ruheposition befindet und der Finger den Joystick ohne Belastung berühren kann. Bringen Sie einen oder zwei zusätzliche externe Schalter an, falls gewünscht, und montieren Sie die Schalter an geeigneten Stellen (z. B. an den Beinen/Zehen/Schultern usw.).

**2. Anschließen des FlipPad an einen Computer, ein Tablet oder ein Smart Phone**

Wenn Sie das FlipPad über das mitgelieferte USB-Mikrokabel anschließen, berühren Sie das Touchpad nicht, solange die LEDs blinken (das anfängliche Blinken zeigt die Phase der Nullpunktkalibrierung an). Warten Sie, bis das Gerät vom Computer erkannt wird, und bewegen Sie dann den Joystick/das Touchpad, um den korrekten Betrieb zu überprüfen.

ball-switch

*Abbildung 11*: Verbinden der FlipPad mit dem Computer

**Bitte beachten Sie**, dass jedes Mal, wenn Sie das FlipPad-Gerät mit Strom versorgen (bzw. wenn Sie es einstecken), eine **Nullkalibrierung** durchgeführt wird, was durch Blinken aller 3 LEDs angezeigt wird. **Es ist wichtig, dass Sie das Touchpad nicht berühren, bis die LEDs nicht mehr blinken.**

#### Verwendung der FlipPad mit Smart Phones oder Tablets

Das FlipPad sollte mit allen Betriebssystemen funktionieren, die USB-HID-Geräte (Maus/Tastatur/Joystick) unterstützen, wie Windows, Linux oder MacOS. Einige Android-Geräte bieten einen USB-Anschluss mit USB-OTG-Funktionalität ("on-the-go"). Wenn Ihr Gerät "OTG" unterstützt, können Sie das FlipPad mit einem USB-OTG-Adapter (siehe Bild unten) anschließen und sie sollte wie eine normale Maus (Sie erhalten einen Mauszeiger) oder Tastatur funktionieren. Sie können mit der App "OTG Checker" testen, ob Ihr Android-Telefon oder Android-Tablet die USB-OTG-Funktion unterstützt.



*Abbildung 12*: Verwendung desFlipPad mit dem Smart Phone

#### Verwendung des FlipPad über Bluetooth

Das Bluetooth - Zusatzmodul für das FlipPad ermöglicht die kabellose Maus-/Tastatursteuerung von Computern, Tablets und Smartphones. Darüber hinaus können iPhones oder iPads über VoiceOver & Assistive-Switch-Unterstützung genutzt werden. Weitere Informationen finden Sie im Kapitel *[Verwendung des Bluetooth-Moduls](https://github.com/asterics/FlipPad/blob/master/Documentation/UserManual/Markdown/FlipPadAnwendungsanleitung.md#verwendung-des-bluetooth-moduls)*.

# FlipPad-Konfigurationsmanager

Der [FlipPad Konfigurationsmanager](https://flippad.asterics.eu/index_pad.htm) bietet eine grafische Benutzeroberfläche (GUI) zum Ändern und Speichern von Einstellungen des FlipPad-Geräts, sodass alle Merkmale und Funktionen an persönliche Vorlieben und Bedürfnisse angepasst werden können. **Derzeit muss der Google Chrome-Browser (oder ein Chromium-basierter Browser) verwendet werden.** Der Konfigurationsmanager ist über die folgende Website zugänglich: **FlipPad.asterics.eu**. Der FlipPad-Konfigurationsmanager sendet und empfängt Informationen von/zu dem FlipPad. Diese Informationsübertragung erfolgt über einen Kommunikationsanschluss (COM-Anschluss). Die folgende Abbildung zeigt die Einstiegsseite des FlipPad-Konfigurationsmanagers:

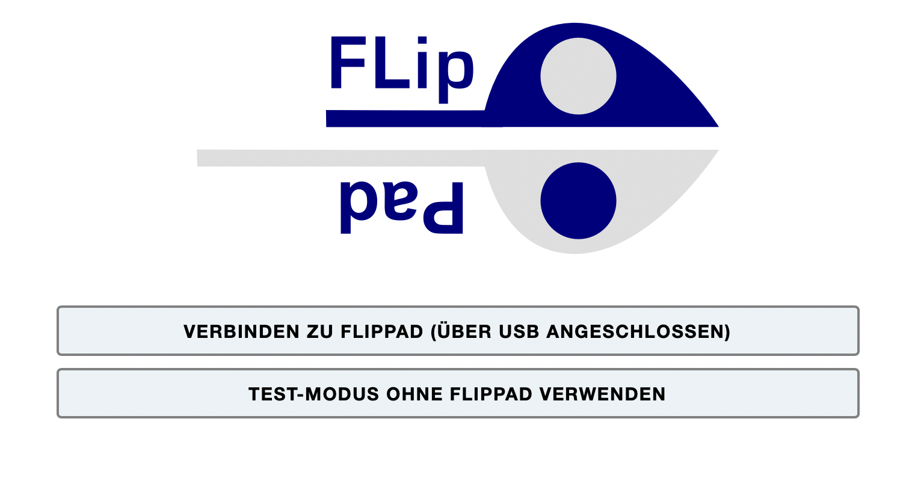
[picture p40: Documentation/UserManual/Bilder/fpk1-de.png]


*Abbildung 13: Willkommensseite des FlipPad-Konfigurationsmanagers*

### Anschließen des FlipPad-Geräts

Gehen Sie folgendermaßen vor, um das Gerät anzuschließen:

1. Vergewissern Sie sich, dass Ihr Gerät über einen USB-Anschluss mit Ihrem Computer verbunden ist (siehe "Hinweise zur ordnungsgemäßen Montage und Verwendung").
2. Klicken Sie auf VERBINDEN ZU FlipPad (ÜBER USB ANGESCHLOSSEN) und wählen Sie im Auswahlfeld den entsprechenden COM-Port (Kommunikationsanschluss) aus. Wenn das Auswahlfeld leer erscheint, bedeutet dies, dass kein Kommunikationsanschluss erkannt wurde. Schließen Sie in diesem Fall das FlipPad-Gerät erneut an und warten Sie, bis der COM-Port aktualisiert wird.
3. Sobald der COM-Port ausgewählt ist, klicken Sie auf die Schaltfläche "Verbinden" am unteren Rand des Auswahlfeldes.
4. Nach erfolgreicher Verbindung des COM-Ports wird das Hauptfenster (siehe Abbildung 14) angezeigt und Sie sollten ein Live-Feedback der Stick-Bewegung sehen. Der Port-Status in der oberen rechten Ecke des Fensters zeigt "verbunden" an:

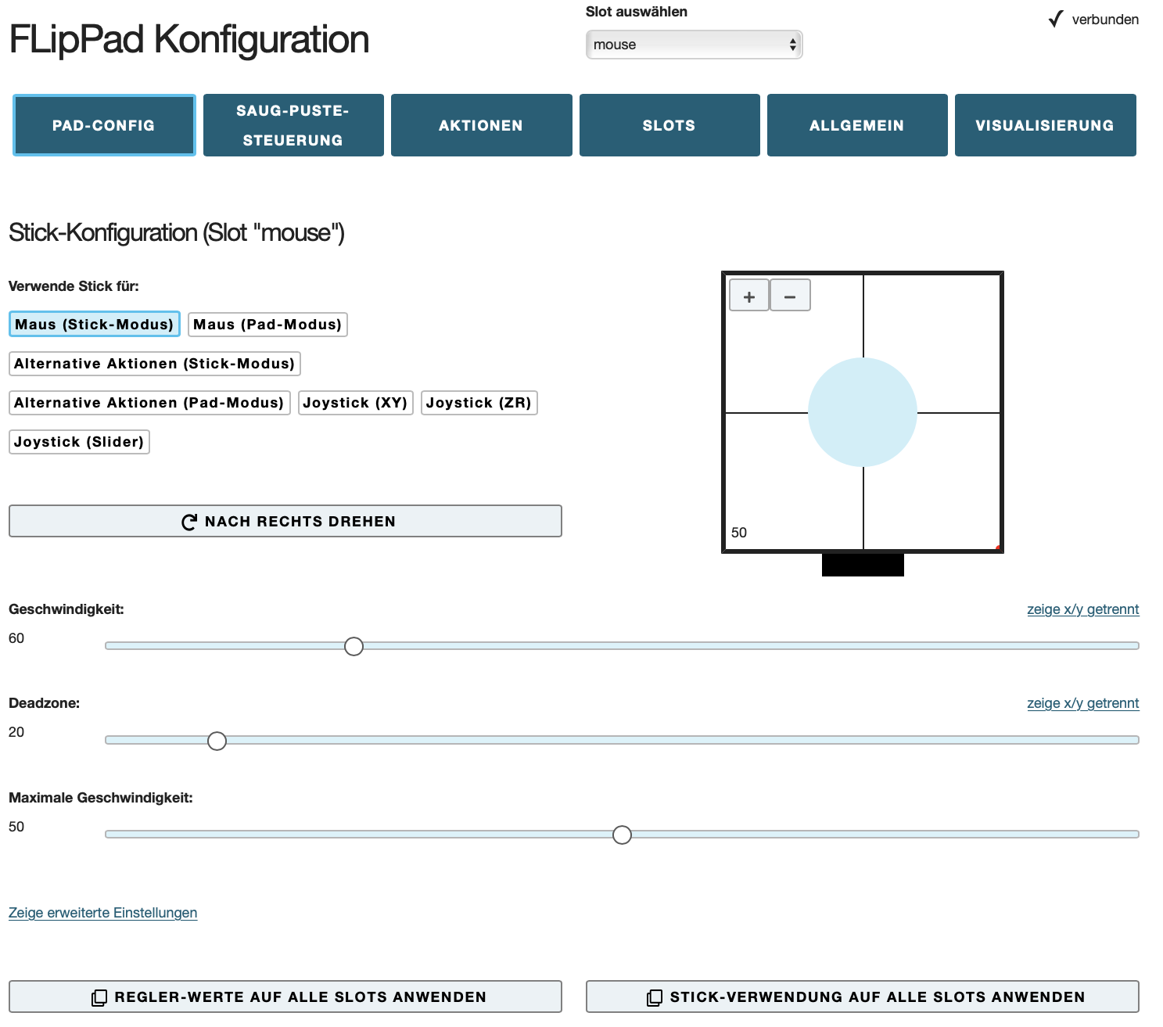
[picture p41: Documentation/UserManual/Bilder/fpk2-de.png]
  

*Abbildung 14*: FlipPad Konfigurationsmanager

## Ändern von Einstellungen und Funktionen

### Betriebsarten - "Speicherplätze"

Der FlipPad-Konfigurationsmanager ermöglicht die Anpassung aller wichtigen Einstellungen (Betriebsmodi). Die Einstellungen werden in einzelnen **Speicherplätzen - "SLOTS"** gespeichert (z.B. ein Slot für schnellen Mausbetrieb, ein Slot für langsamen Mausbetrieb, ein Slot für Tastaturtastengenerierung usw.). Alle Einstellungen können auf dem FlipPad-Gerät gespeichert (oder von dort geladen) werden. Die Einstellungen können auch in einer Datei auf Ihrem Computer gespeichert (oder von dort geladen) werden. Die in dem FlipPad gespeicherten Einstellungen bleiben auch dann gültig, wenn die Stromversorgung / das USB-Kabel entfernt wird. Wenn das FlipPad das nächste Mal eingesteckt wird, sind die Einstellungen wieder verfügbar - auch wenn Sie einen anderen Computer oder ein anderes Betriebssystem verwenden!

### Pad-Konfiguration (Tab PAD-CONFIG)

Im Tab PAD-CONFIG des FlipPad-Konfigurationsmanagers können Sie die *Geschwindigkeit, Deadzone* und *Maximale Geschwindigkeit* des FlipPads ändern. Außerdem können Sie *Beschleunigung, Trackpad-Sensitivtät*, *Maximale Tap-Dauer* und *Maximale Dauer von Tippen + Wischen Gesten* ändern - diese Einstellungen sind nur sichtbar, wenn Sie auf *Zeige erweiterte Einstellungen"* klicken. 

#### Pad-Verwendung definieren (“Verwende Touchpad für”)

Im Tab PAD-CONFIG ganz oben kann die Hauptfunktion des Pads ausgewählt werden. Standardmäßig erzeugt die Pad Mausbewegungen. Das Pad kann jedoch auch für alternative Aktionen verwendet werden (z. B. Drücken der Taste 'A', wenn das Pad nach oben gedrückt wird), die im Tab ACTIONS festgelegt werden können (siehe Abschnitt *[Zuweisung von verschiedenen Aktionen](https://github.com/asterics/FlipPad/blob/master/Documentation/UserManual/Markdown/FlipPadAnwendungsanleitung.md#zuweisung-von-verschiedenen-aktionen-tab-aktionen)*. Außerdem kann der StickMode einen echten Joystick oder ein Gamepad nachahmen (siehe Abschnitt *[Verwendung des Sticks für Joystick-Bewegungen](https://github.com/asterics/FlipPad/blob/master/Documentation/UserManual/Markdown/FlipPadAnwendungsanleitung.md#verwenden-des-sticks-f%C3%BCr-joystick-bewegungen)*.

#### Pad-Ausrichtung (Ändern mit Klick auf "NACH RECHTS DREHEN")

Das FlipPad wird mit einer HotShoe 3/8"-Montageschraube befestigt, die sich an der Unterseite des FlipPad-Gehäuses befindet. Die Ausrichtung kann je nach den Vorlieben des Benutzers geändert werden. Ist die FlipPad z.B. verkehrt herum montiert, kann die Pad-Ausrichtung entsprechend gewählt werden, so dass die Auf/Ab/Links/Rechts-Bewegungen weiterhin korrekt interpretiert werden. Ein Klick auf "NACH RECHTS DREHEN" ändert die Ausrichtung um 90°. Es sind Ausrichtungseinstellungen für 0 / 90 / 180 und 270 Grad möglich, so dass jede Einbaulage möglich ist.

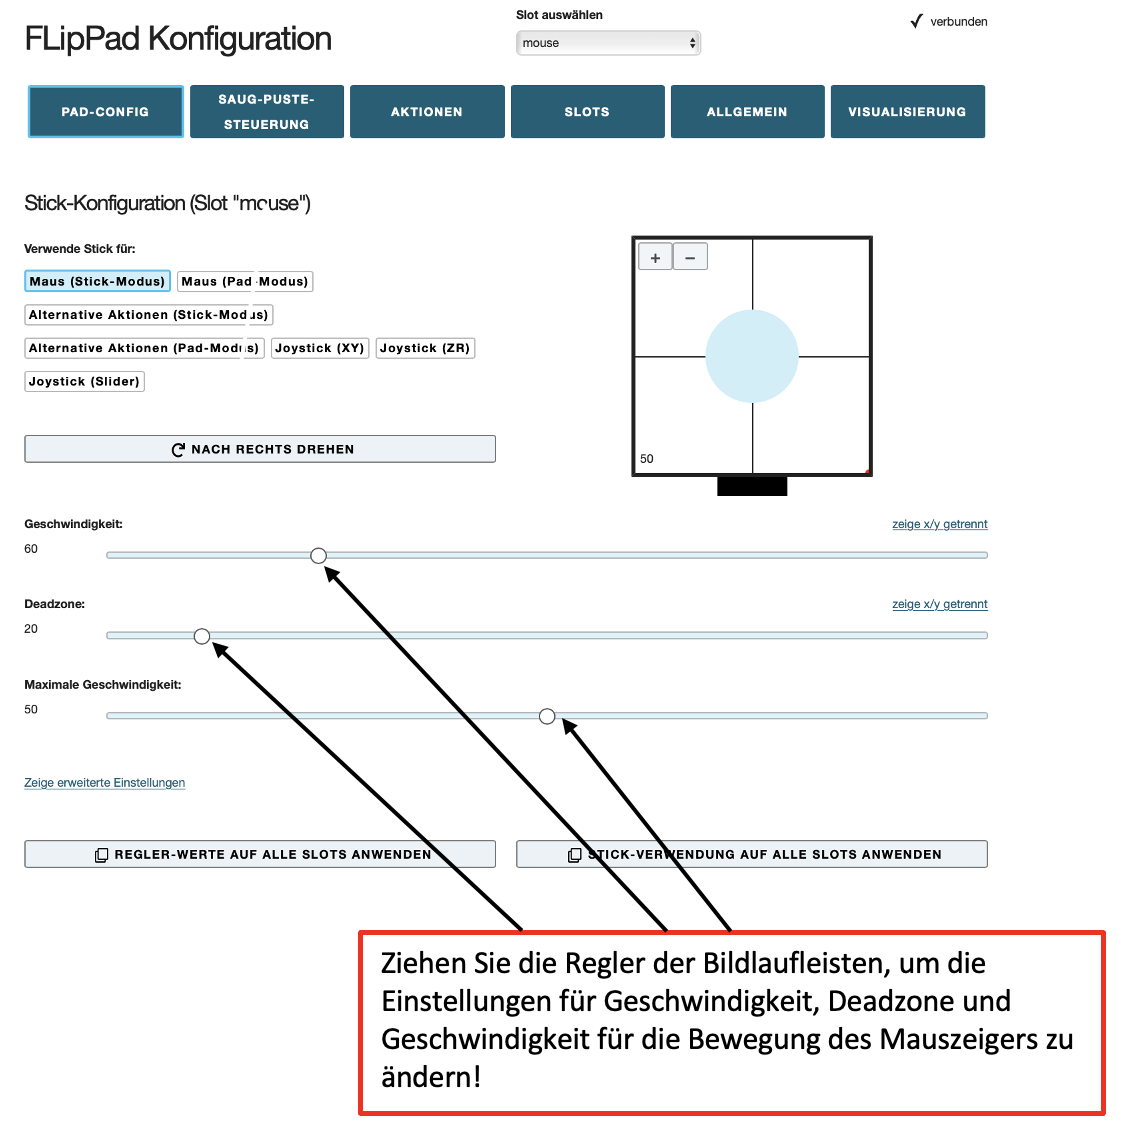
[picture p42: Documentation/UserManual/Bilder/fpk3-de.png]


*Abbildung 15: FlipPad Konfigurationsmanager: Tab PAD-CONFIG, Bildlaufleisten*

Die Bildlaufleisten ermöglichen es, die Parameter des Pads und das Verhalten des Mauszeigers nach den Wünschen des Benutzers / der Benutzerin zu ändern. Das Verhalten der folgenden Merkmale kann geändert werden:

#### Sensitivität

Wenn Sie das Pad für die Cursorbewegung verwenden, kann die Empfindlichkeit des Pads über die Bildlaufleiste *Sensitivität* eingestellt werden. Ein kleinerer Wert führt zu einer langsameren Bewegung des Cursors. Um den Wert zu ändern, klicken und ziehen Sie den Regler der Bildlaufleiste oder klicken Sie auf die Leiste neben dem Regler.

#### Deadzone

Die *Deadzone*-Einstellung definiert einen passiven Bereich für die Padbewegung: Ist der Deadzone-Wert niedrig, führen schon sehr geringe Padbewegungen zu einer Cursorbewegung (oder führen die zugewiesene Alternativfunktion aus - siehe Kapitel *Zuweisung verschiedener Aktionen*). Ist die Deadzone zu niedrig eingestellt, beginnt der Cursor ungewollt zu driften, insbesondere wenn zuvor eine stärkere Kraft aufgewendet wurde. Erhöhen Sie in diesem Fall den Wert der Deadzone, sodass der Cursor unter normalen Betriebsbedingungen für einen bestimmten Benutzer/Benutzerin nicht abdriftet. (Für manche Benutzer / Benutzerinnen könnte es jedoch wünschenswert sein, eine sehr kleine Deadzone zu verwenden, um Cursorbewegungen mit minimaler Kraft zu ermöglichen). Bei anderen Aktionen (z. B. Tastendruck) ist es sinnvoll, einen größeren Wert für die Deadzone zu verwenden, um unbeabsichtigte Aktionen zu vermeiden.

#### Geteilte Achsensteuerung für Sensitivität und Deadzone

Falls gewünscht, können die Sensitivitäts- und Deadzonewerte für horizontale oder vertikale Bewegungen individuell geändert werden. Wählen Sie dazu die Option "*zeige x/y getrennt*", wie unten gezeigt:

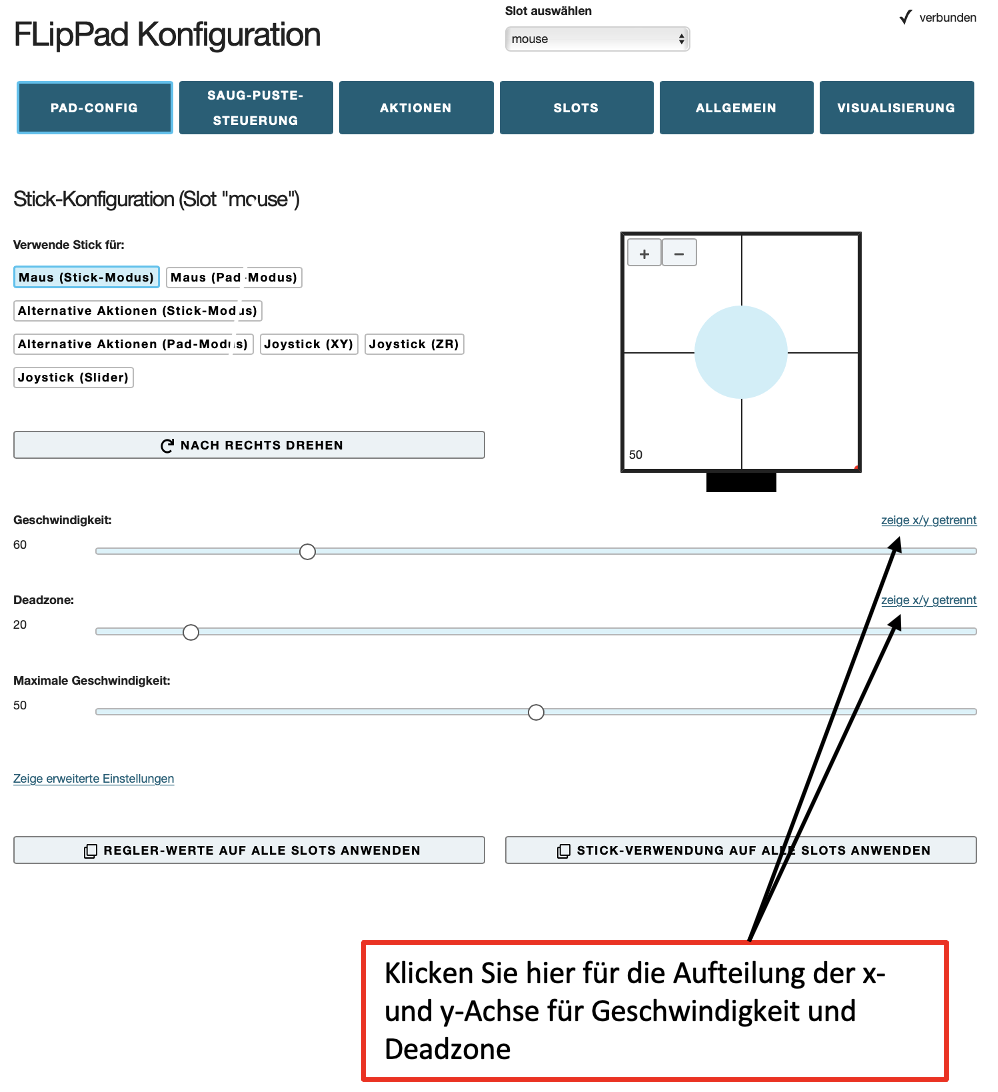
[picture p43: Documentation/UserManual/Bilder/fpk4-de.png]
 *Abbildung 16: FlipPad Konfigurationsmanager: Tab PAD-CONFIG, zeige x/y getrennt*

#### Maximale Geschwindigkeit

Die Einstellung der maximalen Geschwindigkeit auf ein niedriges Niveau ist nützlich, wenn der Benutzer die Cursorgeschwindigkeit begrenzen und gleichzeitig eine hohe Empfindlichkeit/Beschleunigung beibehalten möchte.

**“Zeige erweiterte Einstellungen”**:

#### Trackpad-Sensitivität

Diese Einstellung wird durch Klicken auf *"Zeige erweiterte Einstellungen"* aktiviert. Die Trackpad-Sensitivität erlaubt es, das Beschleunigungsverhalten des Mauszeigers zu beeinflussen: Wenn die Trackpad-Sensitivität auf einen niedrigen Wert eingestellt ist, wird selbst eine starke Auslenkung des Pads eine langsame (aber fortschreitende) Bewegung des Mauszeigers auslösen, was es einfacher macht, kleine Ziele präzise zu erreichen.

### Verwenden des Pads für Joystick-Bewegungen

Wenn Sie im Tab PAD-CONFIG einen der Joystick-Modi auswählen, führt das Bewegen des FlipPads nach oben/unten/links/rechts zu Joystick-Aktivitäten. Das FlipPad verhält sich dann wie ein Gamepad mit 6 Achsen (*X/Y*, *Z/Z-Turn* und *Slider1/Slider2*). Da das FlipPad jeweils nur 2 Achsen Informationen liefern kann, muss die gewünschte Joystick-Achse ausgewählt werden.

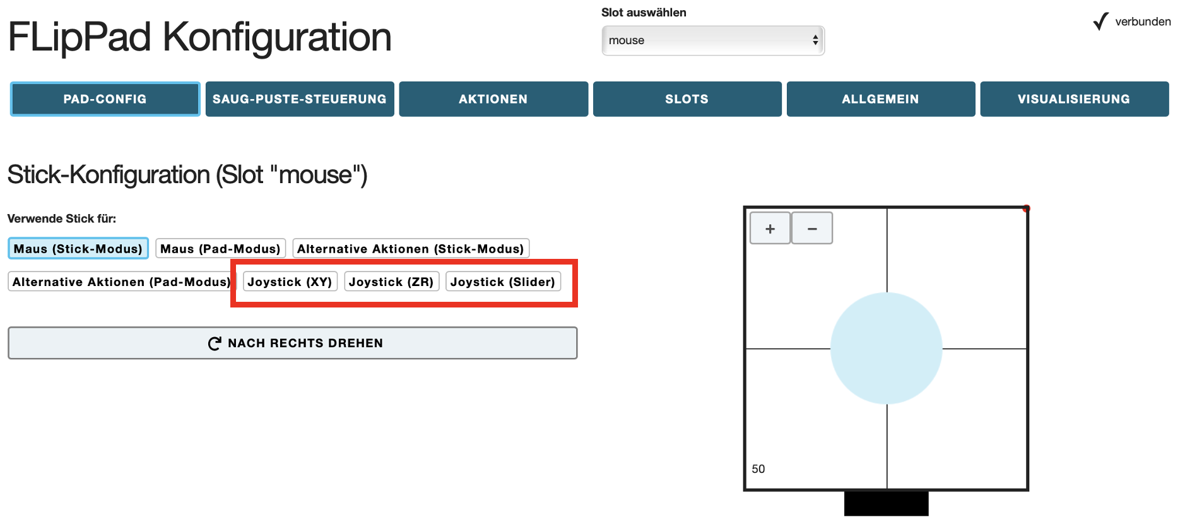
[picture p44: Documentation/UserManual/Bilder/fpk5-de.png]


*Abbildung 18: Padkonfiguration für die Joystick-Bewegung einstellen*

Bitte beachten Sie, dass die Joystick-Funktion von den auf dem Computer laufenden Software-Anwendungen (z.B. Computerspiele) unterstützt werden muss. Microsoft Windows bietet eine Test-Software namens "*joy.cpl*" an - Sie können dieses Programm starten, indem Sie "*joy.cpl*" in den Suchdialog eingeben.

Der von dem FlipPad bereitgestellte Joystick-Controller heißt *"Serial+Keyboard+Mouse+Joystick "*. Wenn Sie dieses Gerät im Dienstprogramm "*joy.cpl*" auswählen, klicken Sie auf die Eigenschaften, um seine Einstellungen anzuzeigen. Die Live-Werte der Joystick-Achsen und der Tastenaktivitäten werden in einem Fenster angezeigt, das dem hier gezeigten ähnelt:



*Abbildung 19: Joy.cpl Eigenschaften*

Gewünschte Joystick-Tasten-Aktivitäten können mit Saug/Puste- oder anderen Interaktionsereignissen erstellt werden, indem Sie "*Joystick ... setzen"* aus dem Aktionsmenü wählen, wie im Abschnitt *[Zuweisung von verschiedenen Aktionen](https://github.com/asterics/FlipPad/blob/master/Documentation/UserManual/Markdown/FlipPadAnwendungsanleitung.md#zuweisung-von-verschiedenen-aktionen-tab-aktionen)*) beschrieben.

### Optional: Saug/Puste Aktionen and Schwellenwerte (Tab SAUG-PUSTE-Steuerung)

Wenn der FlipPad-Stick mit dem Mund verwendet wird, kann der Benutzer Aktionen auslösen, indem er am Mundstück saugt oder pustet. Der Schlauch ist mit einem Drucksensor verbunden, der einen Wert ausgibt, der dem festgestellten Druck entspricht. Wenn der Benutzer saugt, sinkt der Sensorwert, und wenn er pustet, steigt der Wert. Über die Registerkarte "AKTIONEN" können Sie Aktionen für das Saugen oder Pusten zuweisen, wie im nächsten Abschnitt erläutert wird. Die Schwellenwerte für Saugen und Pusten können Sie auf im Tab "SAUG-PUSTE-STEUERUNG"" nach Belieben einstellen. Wenn die FlipPad angeschlossen ist, können Sie in dieser Registerkarte auch die aktuellen Druckwerte und die Auslösung von Saug- und Puste-Aktionen überwachen:

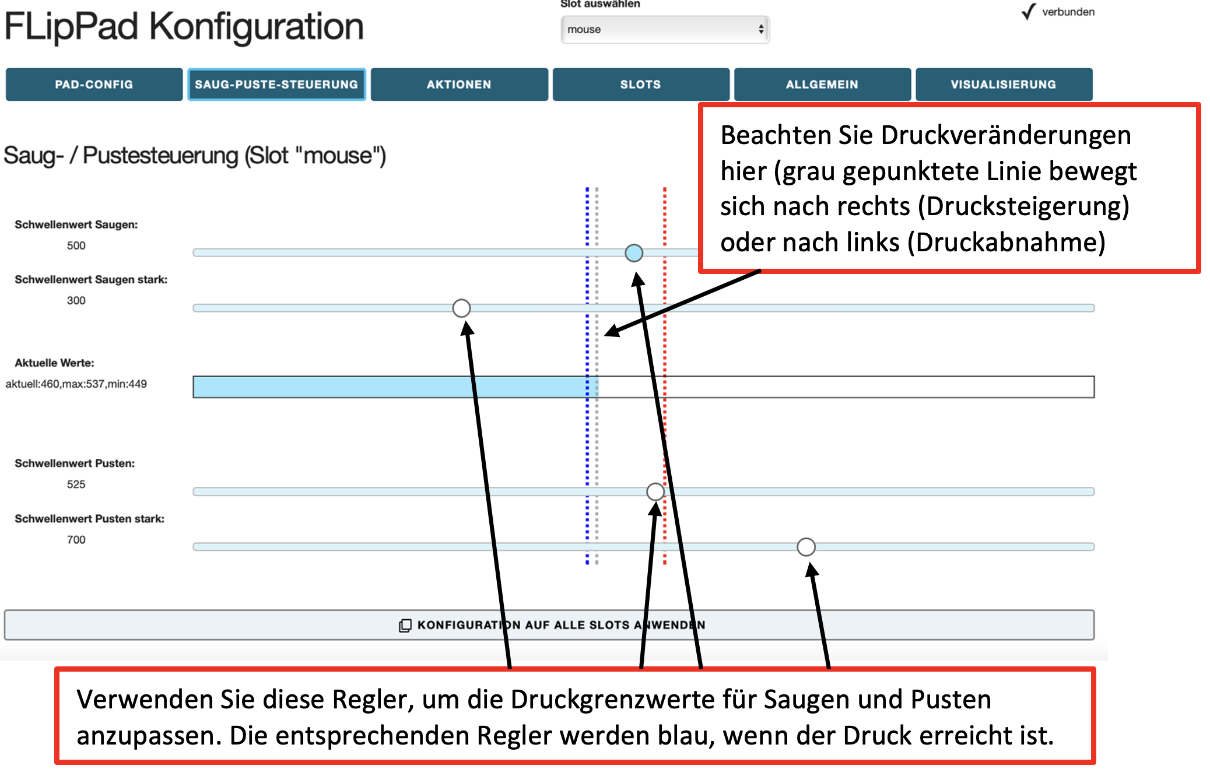
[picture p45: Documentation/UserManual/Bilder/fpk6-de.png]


*Figure 20:* Tab SAUG-PUSTE-STEUERUNG

Beachten Sie, dass der Leerlaufdruck (ohne Saugen und ohne Pusten) bei bei etwa 512 liegt, und der Druck steigt, wenn Sie in das Mundstück pusten, das dadurch auch einen erhöhten Druck anzeigt. Mit den Schiebereglern kann der Schwellendruck für Saugen und Pusten eingestellt werden. Die graue gepunktete Linie stellt den aktuellen Druck dar. Die blaue und die rote gepunktete Linie stellen die in dieser Sitzung erreichten Grenzwerte dar.

#### Stark (An)saugen and Stark Pusten

Im Tab SAUG-PUSTE-STEUERUNG können zusätzliche Schwellenwerte für starkes Saugen und starkes Pusten definiert werden, die dann unterschiedliche Aktionen auslösen können. Zum Beispiel könnte der nächste Slot durch starkes Pusten aktiviert werden. Um die Funktionalität der FlipPad insbesondere für Personen zu erweitern, die nicht auf externe Schalter zugreifen können, sind noch zusätzliche Aktionen verfügbar, die mit starkem Saugen oder starkem Pusten ausgelöst werden. Diese Gesten ermöglichen das Auslösen von Aktionen durch starken Saugen oder starkes Pusten, gefolgt von einer Stick-Bewegung (rauf / runter / links / rechts). Starkes Saugen oder starkes Pusten wird durch ein akustisches Signal (hoher Ton) angezeigt. Wird der Stick innerhalb einer Sekunde bewegt, wird die entsprechende Aktion (z.B. "Stark ansaugen + nach oben") ausgelöst. Wird der Stick nicht innerhalb einer Sekunde bewegt, wird die einzelne Stark pusten- oder Stark ansaugen-Aktion ausgelöst. Insgesamt können also 10 zusätzliche Aktionen ausgeführt werden.

### Zuweisung von verschiedenen Aktionen (Tab AKTIONEN)

Das Tab AKTIONEN ermöglicht die Zuordnung von Benutzeraktivitäten zu gewünschten FlipPad-Funktionen (Aktionen). Die Benutzeraktivitäten sind:

* das Drücken oder Loslassen der 3 Tasten (eingebaute Taste 1 oder externe Taste 2 oder 3)
* Stickbewegungen (auf/ab/links/rechts), die den Schwellenwert der Deadzone überschreiten
* Saug- und Puste-Aktivitäten (siehe Abschnitt *Stark (An)saugen und Stark Pusten*).

Die Aktionen können durch Anklicken des Eintrags in der Aktionskonfigurationstabelle geändert werden (siehe das blaue Feld in Abbildung 21). Die Tabelle zeigt die Aktionen für alle Benutzeraktivitäten an, entweder nur für den gerade aktiven Slot oder für alle Slots (was einen Überblick über alle Aktionen gibt). Wenn Sie auf eine bestimmte Aktion klicken, öffnet sich ein Fenster, in dem Sie die Aktionskategorie (in Abbildung 22 für Button 1: Gerät) und die Aktion selbst (hier: Nächsten Slot laden) ändern können, siehe Abbildung 22.

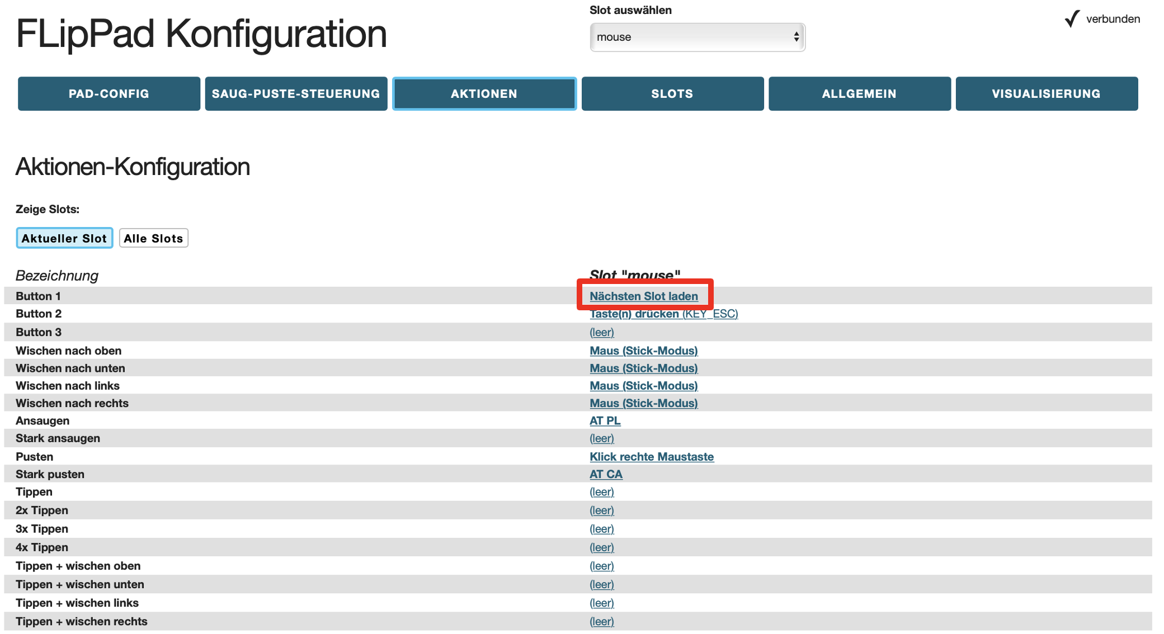
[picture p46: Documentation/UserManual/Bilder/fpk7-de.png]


*Abbildung 21: Benutzeraktivitäten verschiedene Aktionen zuordnen*

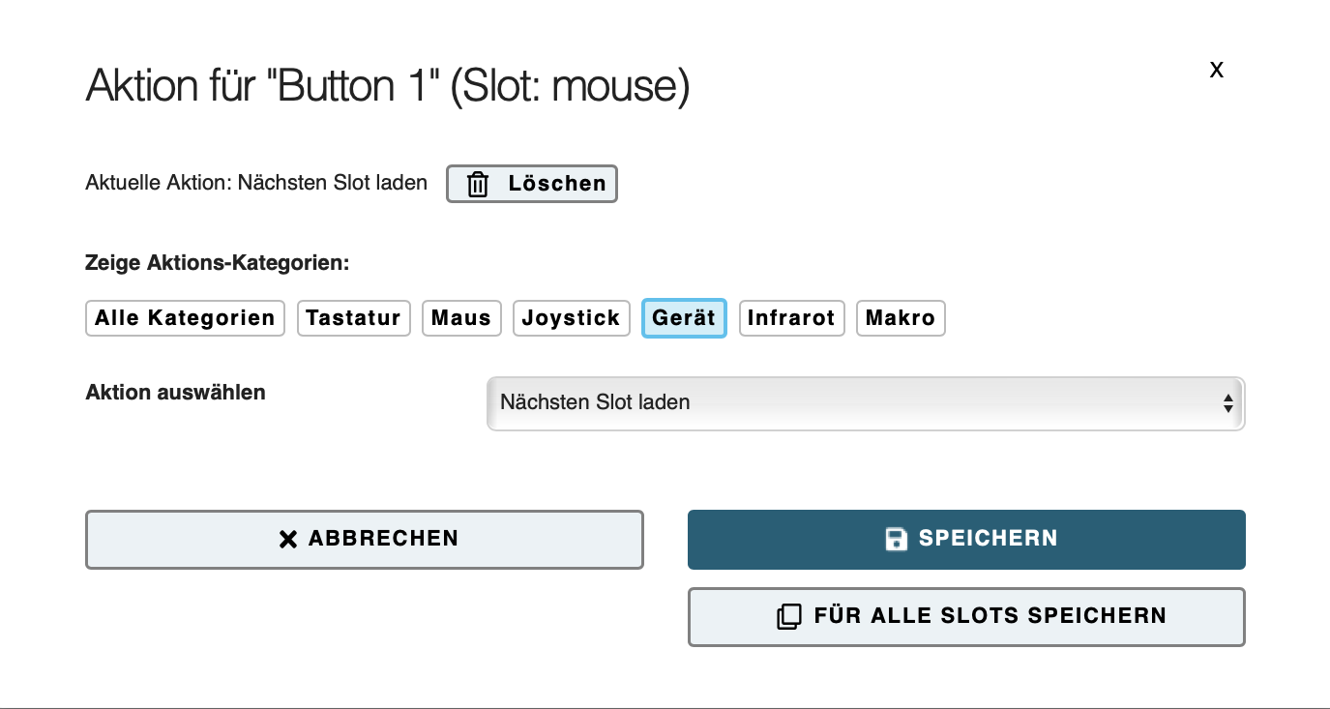
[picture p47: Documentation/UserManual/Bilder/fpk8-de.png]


*Abbildung 22: Pop-up-Fenster zur Auswahl der gewünschten Aktion*

Im Folgenden werden die einzelnen Aktionskategorien und die verschiedenen Aktionen kurz beschrieben.

#### Aktionskategorie “Maus”

**Linke / Mittlere / Rechte Maustaste halten (für die Dauer der Eingabe-Aktion)** Bei der Aktion *Halten* wird eine bestimmte Maustaste kontinuierlich gedrückt (z. B. um ein Element über den Bildschirm zu ziehen). Die Maustaste wird losgelassen, wenn die zugewiesene Benutzeraktivität endet (z. B. wenn die Aktivität "Saugen/Pusten" endet, wenn der Stick wieder in die mittlere Position gebracht wird oder wenn eine externe Taste losgelassen wird).

**Klick linke / mittlere / rechte Maustaste** Mit diesen Funktionen kann ein Klick der linken, rechten oder mittleren Maustaste ausgeführt werden. **Anmerkung:** ein Klick besteht aus drücken & loslassen der entsprechenden Maustaste, beides passiert kurz hintereinander nach Betätigen des Tasters / Bewegen des Pads / Saug-/Pustesteuerung!

**Doppelklick linke Maustaste** Erzeugt einen Doppelklick mit der linken Maustaste. Ein Doppelklick der linken Maustaste ist zum Beispiel zum Öffnen einer Datei notwendig. Das Ausführen von schnellen Mausklicks kann jedoch für manche NutzerInnen schwierig sein.

**Drücken oder Loslassen linke / mittlere / rechte Maustaste (umschalten)** Die Aktion *Umschalten* ändert den Zustand einer Maustaste von gedrückt zu nicht gedrückt und umgekehrt. Dies ist z. B. nützlich, wenn eine Benutzeraktivität länger aufrechterhalten werden soll (z. B. beim Ziehen eines Objekts oder um eine Taste gedrückt zu halten, während andere Tasten gedrückt/losgelassen werden). Beachten Sie, dass die Maustaste solange gedrückt bleibt, bis die zugewiesene Benutzeraktivität ein weiteres Mal aufgerufen wird!

**Nach oben / unten scrollen** Die Aktionen *Nach oben / unten scrollen* ahmen das Maus-Scrollrad nach. Das Auslösen der Aktion *Nach oben scrollen* führt zu einem Bildlauf nach oben, während *Nach unten scrollen* zu einem Bildlauf nach unten führt. Diese Aktion ist zum Beispiel beim Lesen von Dokumenten oder Webseiten nützlich.

**Maus horizontal / vertikal bewegen (x-Achse / y-Achse)** Die Funktionen *Maus horizontal bewegen (x-Achse)* und *Maus vertikal bewegen (y-Achse)* erzeugen Computermausbewegungen entlang der ausgewählten Achsen. Die Geschwindigkeitsparameter für diese Funktionen können in dem darunter erscheinenden Feld eingestellt werden. Solange die Benutzeraktivität vorhanden ist, wird der Mauszeiger bis zu dieser maximalen Geschwindigkeit beschleunigt. Bitte beachten Sie dies:

*Ein positiver Wert für die X-Richtung bewegt den Mauszeiger nach rechts. Ein negativer Wert für die X-Richtung verschiebt den Mauszeiger nach links. Ein positiver Wert für die Y-Richtung verschiebt den Mauszeiger nach unten. Ein negativer Wert für die Y-Richtung bewegt den Mauszeiger nach oben.*

#### Aktionskategorie "Joystick"

**Joystick x-/y-/z-Achse/z-Drehung/Regler setzen** Diese Aktionen können verwendet werden, um einen gewünschten Wert an die Joystick-Achse zu senden. Die wählbaren Joystick-Achsen sind: *X / Y / Z / Z-Drehung / Regler*. Der Joystick wird in die Mittelstellung zurückbewegt, wenn die zugehörige Benutzeraktivität endet.

**Joystick-Button halten (für Dauer der Eingabe-Aktion)** Diese Aktion kann verwendet werden, um einen gewünschte Joystick-Button zu drücken. Das FlipPad-Gerät unterstützt 32 Tasten, so dass jeder Wert von 1 bis 32 zulässig ist. Der Joystick-Button wird losgelassen, wenn die zugehörige Benutzeraktivität beendet ist.

**Joystick Hat-Position setzen** Mit dieser Aktion wird die Ausrichtung des Joystick-"Hats" (in Grad) festgelegt. Erlaubte Werte sind: *-1, 0, 45, 90, 135, 180, 225, 270, 315*. Der Wert -1 setzt den Hat auf die mittlere Position (Leerlauf). Der Joystick-Hat wird in die Mittelstellung zurückbewegt, wenn die zugehörige Benutzeraktivität endet.

#### Aktionskategorie "Tastatur"

**Taste(n) drücken + wieder loslassen / halten / umschalten** Die Aktion *Taste(n) drücken + wieder loslassen* ermöglicht das Drücken einer oder mehrerer Tastaturtasten. Es wird ein zweites Dropdown-Menü mit möglichen Tastenbezeichnungen angezeigt (***Tasten hinzufügen***). **Wenn eine Taste aus diesem Menü ausgewählt wird, muss sie in das Feld *Eingabe Tasten* eingefügt werden (auf HINZUFÜGEN klicken)**. Auf diese Weise können mehrere Tasten der Tastatur gleichzeitig gedrückt werden. Die Taste(n) wird kurz darauf wieder losgelassen. Wenn Sie die zugewiesenen Tasten entfernen oder ändern möchten, müssen Sie die aktuell zugewiesenen Tasten löschen, indem Sie auf die Schaltfläche "LÖSCHEN" neben dem Feld *Eingabe Tasten* einfügen klicken.

Gängige Tastenkombinationen sind: TASTE_CTRL + Z: löst die Rückgängig-Funktion aus TASTE_CTRL + C: löst die Kopierfunktion aus KEY_CTRL + V: löst die Einfügefunktion aus KEY_CTRL + KEY_ALT + KEY_ DELETE

Die Aktion *Taste(n) halten (für Dauer der Eingabe-Aktion)* hält die Taste gedrückt, bis die Benutzeraktivität beendet ist. Die Aktion *Taste(n) drücken oder auslassen (umschalten)* wechselt bei jeder Benutzeraktivität den Zustand der Taste von gedrückt zu nicht gedrückt und umgekehrt.

Eine Liste aller unterstützten Tastenbezeichner finden Sie im [Anhang](https://github.com/asterics/FlipPad/blob/master/Documentation/UserManual/Markdown/FlipPadAnwendungsanleitung.md#liste-der-k%C3%BCrzel-f%C3%BCr-keybord-tasten) oder werfen Sie einen Blick auf die [FlipPad Wiki / Github Seiten](https://github.com/asterics/FlipPad/wiki/at-api).



*Abbildung 23: Hinzufügen von Tasten für die Aktionen Tasten Drücken / Halten / Umschalten*

**Schreibe Wort** Die Aktion *Schreibe Wort* ermöglicht die Eingabe eines bestimmten Textes/Satzes bei zugewiesener Benutzeraktivität (z. B.: Schreiben Sie "Hallo", wenn Sie den FlipPad-Stick nach oben bewegen). Wenn Sie diese Aktion auswählen, wird unter dem Dropdown-Menü ein leeres Textfeld angezeigt, in das der Text eingegeben werden kann (siehe unten):



*Abbildung 24: Funktion Schreibe Wort*

In diesem Beispiel wird jedes Mal, wenn die Taste 1 der FlipPad gedrückt wird, "Hallo" geschrieben.

#### Aktionskategorie "Gerät"

**Keine Funktion (leer)** Wenn die Aktion *Keine Funktion (leer)* ausgewählt ist, wird der entsprechenden Benutzeraktivität keine Aktion zugewiesen.

**Nächsten Slot laden** Diese Aktion ist nur relevant, wenn Sie mehrere FlipPad-Konfigurations-Slots gespeichert haben. Diese Aktion schaltet auf den nächsten Slot um. Wenn der letzte Slot bereits erreicht ist, wird durch Auslösen dieser Aktion zum ersten Slot gewechselt. Wenn Sie den Steckplatz wechseln, ändern sich die eingebauten LED-Lampen entsprechend und zeigen den aktiven Steckplatz an.

Es gibt drei eingebaute LEDs (rot, gelb-orange, grün), die die Binärzahl für die Steckplatzposition der von Ihnen gewählten Konfiguration anzeigen. Wenn Sie also zwei Konfigurationen gespeichert haben, z.B. "Spieleinstellungen" und "Maus", dann ist "Spieleinstellungen" der Slot 1 und "Maus" der Slot 2.

Zusätzlich zu den LEDs wird der Wechsel des Steckplatzes durch ein akustisches Signal angezeigt.

Die folgende Liste zeigt die Farbcodes und die akustischen Signale der LEDs für jede Steckplatzposition:

| **Aktiver Slot** | **Akkustisches Signal** | **Aufleuchtende LEDs** | | ---------------- | ----------------------- | ---------------------- | | Slot 1 | ein Biepton | rot | | Slot 2 | zwei Bieptöne | gelb | | Slot 3 | drei Bieptöne | rot, gelb | | Slot 4 | vier Bieptöne | grün | | Slot 5 | fünf Bieptöne | rot, grün | | Slot 6 | sechs Bieptöne | gelb, grün | | Slot 7 | sieben Bieptöne | rot, gelb, grün |

Die nächste Abbildung (Abbildung 25) zeigt eine ähnliche Liste, aber die leuchtenden LEDs in den entsprechenden Farben für die visuellen Menschen. Die verschiedenen Slots werden in dieser Abbildung als "Position" bezeichnet.

buttons

*Abbildung 25: Farbcodes der LEDs*

**Slot per Name laden** Mit dieser Aktion wird der Konfigurations-Slot mit dem angegebenen Namen aktiviert. Der Name kann im Drop-Down Menü ausgewählt werden. Diese Aktion ist nur relevant, wenn Sie mehrere FlipPad-Konfigurations-Slots gespeichert haben. Die LEDs zeigen die Slotnummer wie oben beschrieben an.

**Stick-Mittelposition kalibrieren** Diese Aktion startet die Kalibrierungssequenz für die mittlere Position des Sticks. Bitte beachten Sie die Beschreibung ["](https://github.com/asterics/FlipPad/blob/master/Documentation/UserManual/Markdown/FlipPadAnwendungsanleitung.md#kalibrierung-der-mittelposition-des-sticks)*[Kalibrierung der Mittelposition des Sticks](https://github.com/asterics/FlipPad/blob/master/Documentation/UserManual/Markdown/FlipPadAnwendungsanleitung.md#kalibrierung-der-mittelposition-des-sticks)*["](https://github.com/asterics/FlipPad/blob/master/Documentation/UserManual/Markdown/FlipPadAnwendungsanleitung.md#kalibrierung-der-mittelposition-des-sticks).

#### Aktionskategorie: "Infrarot"

**Infrarot-Kommando abspielen / halten** Diese Aktion gibt den Infrarot (IR-)Code mit dem angegebenen Befehlsnamen wieder. Die vorhandenen (aufgezeichneten) IR-Befehle können aus dem Dropdown-Menü ausgewählt werden. Die Aktion *Infrarot-Kommando abspielen* sendet den aufgezeichneten Code einmal, während die Aktion *Infrarot-Kommando halten* den Code wiederholt, bis die Benutzeraktivität beendet ist. Weitere Informationen zu Infrarot-Codes finden Sie im Abschnitt ["](https://github.com/asterics/FlipPad/blob/master/Documentation/UserManual/Markdown/FlipPadAnwendungsanleitung.md#infrarot-code-aufzeichnung-und--wiedergabe)*[Infrarot-Code-Aufzeichnung und -Wiedergabe](https://github.com/asterics/FlipPad/blob/master/Documentation/UserManual/Markdown/FlipPadAnwendungsanleitung.md#infrarot-code-aufzeichnung-und--wiedergabe)*["](https://github.com/asterics/FlipPad/blob/master/Documentation/UserManual/Markdown/FlipPadAnwendungsanleitung.md#infrarot-code-aufzeichnung-und--wiedergabe).

#### Aktionskategorie: Makro

**Benutzderdefiniertes Makro** Diese Aktion ermöglicht das Ausführen eines sogenannten benutzerdefiniertem Makro, das aus mehreren Einzelaktionen besteht. Damit kann eine gewünschte Abfolge von Aktionen ausgeführt werden, die z.B. aus einer Anzahl von Mausbewegungen, Mausklicks, Texteingaben oder Tastendrücken besteht. Diese Aktion ist mächtig, aber auch etwas komplizierter, da die einzelnen Aktionen in Form von sogenannten AT-Befehlen angegeben werden müssen, die durch Semikolons getrennt sind. Ein Beispiel: Das folgende Befehlsmakro bewegt den Mauszeiger 100 Schritte nach links, 20 Schritte nach oben, wartet dann 100 Millisekunden und führt dann einen linken Mausklick aus: "MX 100; MY -20; WA 100; CL". Eine Liste und detaillierte Erklärung aller unterstützten AT-Befehle finden Sie im [Anhang](https://github.com/asterics/FlipPad/blob/master/Documentation/UserManual/Markdown/FlipPadAnwendungsanleitung.md#liste-der-unterst%C3%BCtzten-makrokommandos) oder auf den [FlipPad Wiki / Github Seiten](https://github.com/asterics/FlipPad/wiki/at-api).

### Speicherplätze verwalten (Tab SLOTS)

Im Tab SLOTS können Sie neue Konfigurations-Speicherplätze (Slots) erstellen, vorhandene Slots löschen, einen einzelnen oder alle Slots herunterladen und eine Datei hochladen, die eine vollständige Konfiguration mit mehreren Slots enthält. Nach dem Start des FlipPad-Konfigurationsmanagers ist nur ein Standard-Slot namens "mouse" vorhanden. Wenn Sie mit der Schaltfläche "SLOT ANLEGEN" einen Slot erstellen, wird **der aktuelle Slot kopiert und an den letzten vorhandenen Slot angehängt**. Bevor Sie den neuen Slot erstellen, vergeben Sie im entsprechenden Feld ("Name für neuen Slot eingeben") einen Namen, der Ihnen hilft, sich an den Zweck des Slots zu erinnern:



*Abbildung 26: FlipPad Konfigurationsmanager: Tab SLOTS*

Oben in der Mitte des Fensters des Konfigurationsmanagers (blaues Kästchen in Abbildung 26) wird der aktuelle Slot angezeigt und kann geändert werden. Die Einstellungen des aktuellen Slot werden gespeichert und beim Wechsel zu einem anderen Slot beibehalten. Die maximale Anzahl von Slots beträgt 10.

**Löschen eines Slots** Ein Slot kann über die Schaltfläche *Löschen* neben dem entsprechenden Slot entfernt werden.

**Laden und Speichern der Konfiguration in/aus Datei** Die Schaltfläche *Alle Slots herunterladen* ermöglicht das Übertragen aller aktuellen Slots in eine Einstellungsdatei (.set), die auf Ihrem Computer gespeichert wird. Alle Einstellungen können so auf dasselbe oder auf ein anderes FlipPad-Gerät übertragen werden. Mehrere Einstellungen (z. B. für einzelne Benutzer oder Anwendungsfälle) können auf einem Computer gespeichert und mit einem einzigen Klick übernommen werden. Es wird ein Dateiauswahlfenster geöffnet, in dem der gewünschte Dateiname zum Speichern oder Laden der Konfiguration eingegeben werden kann.

### Allgemeine Einstellungen (Tab ALLGEMEIN)

Im Tab ALLGEMEIN können Sie den USB/Bluetooth-Modus ändern und Firmware-Updates für das FlipPad-Gerät und das Bluetooth-Zusatzmodul (falls installiert) durchführen:

general

*Abbildung 27: Allgemeine Einstellungen*

#### USB/Bluetooth-Modus

Diese Einstellung ist nur relevant, wenn ein Bluetooth-Zusatz-Modul verwendet wird (siehe [FlipPad Wiki-Seiten](https://github.com/asterics/FlipPad/wiki/bt-conn) für weitere Informationen). Mit dieser Auswahlbox kann festgelegt werden, ob die Maus-/Tastaturaktionen eines bestimmten Slots über ein USB-Kabel, über eine Bluetooth-Verbindung oder über beide gesendet werden. So können dedizierte Slots für USB und Bluetooth erstellt werden, so dass ein Benutzer / eine Benutzerin z.B. von einem Laptop (an dem die FlipPad per Kabel angeschlossen ist) zu einer drahtlosen Verbindung (Telefon / Tablet) und zurückwechseln kann.

#### FlipPad Firmware ("UPDATE FIRMWARE")

Hier können Sie die installierte und die verfügbare Version der FlipPad-Software (Firmware) sehen. Wenn die installierte Version älter ist als die Version, die online im FlipPad-Github-Repository verfügbar ist, wird in der Schaltflächenüberschrift "UPDATE FIRMWARE" angezeigt. Wenn Sie auf die Schaltfläche klicken, wird versucht, die neueste Firmware herunterzuladen und zu installieren. Wenn die installierte Version neuer oder identisch mit der verfügbaren Version ist, wird in der Schaltflächenbeschriftung "FIRMWARE ÜBERSCHREIBEN" angezeigt. - Wenn Sie auf die Schaltfläche klicken, wird auch die online verfügbare Version heruntergeladen und installiert.

#### Firmware Bluetooth-Add-on ("UDPATE BLUETOOTH-FIRMWARE")

Hier können Sie die installierte und die verfügbare Version der Firmware des Bluetooth-Add-On-Moduls sehen. Ähnlich wie bei der FlipPad-Firmware-Aktualisierung können Sie auf die Schaltfläche "UPDATE BLUETOOTH FIRMWARE / BLUE-TOOTH FIRMWARE ÜBERSCHREIBEN" klicken, wodurch versucht wird, die neueste Software (Firmware) für das Bluetooth-Modul herunterzuladen und auf dem Modul zu installieren. Dieser Vorgang kann einige Minuten dauern und ist nur möglich, wenn ein Bluetooth-Modul an die FlipPad angeschlossen ist. Wenn kein Bluetooth-Modul an die FlipPad angeschlossen ist, wird eine Meldung angezeigt, dass die installierte Version unbekannt ist.

### Kraftstufen anzeigen (Tab VISUALISIERUNG)

Der FlipPad-Stick ist mit vier Kraftsensoren verbunden - einer für jede Bewegungsrichtung (oben, unten, links, rechts). Der numerische Wert jedes dieser Sensoren wird auf der Registerkarte "VISUALISIERUNG" angezeigt. Die aktuellen Werte können überwacht werden, wenn das FlipPad-Gerät angeschlossen ist. Wenn der Stick bewegt wird, ändern sich die Sensorwerte. Insbesondere erhöht eine Bewegung in jede Richtung den jeweiligen Sensorwert. Die Sensorwerte hängen auch von der Verwendung der Einstellschrauben ab, die die Kraft verändern, die über 4 Metallfedern auf die Sensorpads ausgeübt wird. Daher sollten beim Zusammenbau der FlipPad die aktuellen Sensorwerte als Richtwerte verwendet werden. **Wenn der Stick nicht berührt wird, sollten die Werte ähnlich wie auf dem Screenshot unten aussehen. Alle Werte sollten in ähnlicher Weise sinken und steigen, wenn der Stick bewegt wird. Signifikante Abweichungen in eine Richtung deuten auf ein Sensorproblem hin. Die Sensoren sollten überprüft werden und müssen möglicherweise ausgetauscht werden.**

visualisation

*Abbildung 28: Links: Live-Anzeige der Kraftsensorwerte; Mitte: aktueller Slot mit den 3 Tasten (wenn eine Taste gedrückt wird, wird der entsprechende Kreis gelb); Rechts: Sip und Puff Live-Wert und aktuelle Schwellenwerte*

### Infrarot-Code-Aufzeichnung und -Wiedergabe

Die FlipPad verfügt über ein Infrarot-Fernbedienungs-Empfängermodul und eine Hochstrom-IR-LED, sodass sie Fernbedienungscodes vieler in der Unterhaltungselektronik verwendeter Fernbedienungsgeräte aufzeichnen und wiedergeben kann. Wenn Sie diese Funktion der FlipPad nutzen möchten, achten Sie darauf, dass die IR-Sende-LED auf das zu steuernde Gerät gerichtet ist. Eine Anleitung zum Anschluss einer externen IR-LED zur Erhöhung der Sendeleistung finden Sie auf den [FlipPad Wiki-Seiten](https://github.com/asterics/FlipPad/wiki).

infrared

*Abbildung 29: Infrarot-Code-Aufzeichnung*

Um einen neuen IR-Code aufzuzeichnen, gehen Sie auf die Registerkarte AKTIONEN. Klicken Sie auf die gewünschte Aktion und wählen Sie im Popup-Fenster die Aktionskategorie "**Infrarot**". Dort können zwei verschiedene Arten von IR-Aktionen aus dem Kombinationsfeld ausgewählt werden:

* *Infrarot-Kommando abspielen*: sendet den aufgezeichneten Code einmal
* *Infrarot-Kommando halten (für Dauer der Eingabe-Aktion)*: wiederholt den Code, bis die Benutzeraktivität beendet ist

Die vorhandenen Befehle können aus dem Dropdown-Menü ausgewählt werden.

In diesem Fenster können Sie auch IR-Kommandos verwalten. Neben *Neues IR-Kommando* können Sie einen Namen eingeben und dann auf AUFNAHME klicken - richten Sie Ihre IR-Fernbedienung auf die Seite der FlipPad, an der die LEDs herausragen, und senden Sie den IR-Befehl (für die Aufzeichnungsphase gibt es ein Zeitlimit von 10 Sekunden). Der neue Befehl wird nun in der FlipPad gespeichert und kann durch Auswahl des Namens im Dropdown-Menü ausgewählt und wiedergegeben werden. Wenn der Befehl nicht korrekt wiedergegeben wird, versuchen Sie, den IR-Code-Timeout zu erhöhen - zum Beispiel auf 250 Millisekunden ("Zeige erweiterte Optionen"). Mit *IR Kommando Löschen* können Befehle gelöscht werden.



*Abbildung 30: Konfigurationsmanager für Infrarot-Aufnahme und -Wiedergabe*

# Verwendung des Bluetooth-Moduls

Das optionale Bluetooth-Zusatzmodul ermöglicht den Anschluss und die Steuerung von Handys, Tablets und Computern mit Bluetooth-Fähigkeit. Wenn die FlipPad über USB an einen PC oder Laptop angeschlossen ist, kann der Benutzer auf Bluetooth-Betrieb umschalten und bei Bedarf wieder auf USB. Das Bluetooth-Modul ist separat bei der AsTeRICS Foundation erhältlich oder in der entsprechenden Version des FlipPad-Kits enthalten.

#### Einbau des Bluetooth-Moduls

Das Bluetooth-Modul wird auf den internen 10-poligen Anschluss der FlipPad gesteckt. Öffnen Sie dazu das FlipPad-Gehäuse und schieben Sie das Modul so weit wie möglich auf die Stiftleiste:


Wird morgen gemacht!!
*Abbildung 31: Bluetooth-Modul*

#### Verbinden mit einem Bluetooth-Host-Gerät (Pairing)

Das Host-Gerät kann z. B. ein Mobiltelefon mit Android- oder iOS-Betriebssystem sein. Die FlipPad kann nur dann mit einem Host-Gerät verbunden werden, wenn derzeit kein Gerät verbunden ist und somit der Pairing-Modus aktiv ist. Um ein Gerät zu verbinden, öffnen Sie die Bluetooth-Einstellungen Ihres Android- oder iOS-Geräts, aktivieren Sie BT, wählen Sie *neues BT-Gerät hinzufügen* und wählen Sie die FlipPad aus der Liste der verfügbaren Geräte aus. Öffnen Sie dann die Registerkarte ALLGEMEIN und aktivieren Sie den Bluetooth-Betrieb für die gewünschten Slots (siehe Abschnitt *[Allgemeine Einstellungen](https://github.com/asterics/FlipPad/blob/master/Documentation/UserManual/Markdown/FlipPadAnwendungsanleitung.md#allgemeine-einstellungen-tab-allgemein)*.

Hinweis: Wenn sich das Bluetooth-Modul im Paring-Modus befindet, blinkt die LED des Moduls schnell (ca. zweimal pro Sekunde). Wenn eine Verbindung hergestellt ist, blinkt die LED langsam (ca. einmal alle 2 Sekunden). Die LED ist nur zu sehen, wenn das Gehäuse der FlipPad geöffnet ist.

# Aktualisieren der Firmware über die Arduino IDE

Neben der Möglichkeit, die FlipPad-Firmware über den Konfigurationsmanager zu aktualisieren, kann die Firmware auch über die Arduino-IDE und die Teensyduino-Add-on/Loader-Anwendung aktualisiert werden. Die neuesten Versionen finden Sie im aktuellen Release-Paket auf [Github](https://github.com/asterics/FlipPad/releases). Entpacken Sie das Paket FlipPad.zip und starten Sie das Programm teensy.exe (den Teensy Loader).



*Abbildung 34: Teensy Loader Schritt 1*

Die Benutzeroberfläche des Teensy Loader sollte wie in Abbildung 34 dargestellt aussehen. Falls eine Sicherheitswarnung (im Zusammenhang mit der Windows-Benutzerzugriffskontrolle) erscheint, stellen Sie bitte sicher, dass der Herausgeber "PJRC.COM, LLC" ist und klicken Sie auf "Ausführen". Aktivieren Sie im nächsten Schritt den "Download-Modus" der FlipPad, indem Sie mit einem spitzen Gegenstand (Nadel, kleiner Schraubenzieher, ...) auf die Reset-Taste drücken, die über das kleine Loch an der Unterseite der FlipPad zugänglich ist. Nach ein paar Sekunden (Treiberinstallation) sollte die Teensy Loader GUI die Verbindung zur FlipPad anzeigen, wie in der folgenden Abbildung dargestellt:



*Abbildung 35: Teensy Loader Schritt 2*

Wählen Sie "File → Open HEX file" (Datei → HEX-Datei öffnen) und wählen Sie die Datei "FLipWare.hex" aus dem FlipPad-Ordner (oder dem Ort, an dem Sie die .zip-Datei heruntergeladen haben).

Wählen Sie "Betrieb → Programm". Nach ein paar Sekunden sollten Sie die Meldung "Download abgeschlossen" sehen, so wie in der nächsten Abbildung (Abbildung 36). (Wenn dieser Schritt nicht funktioniert, versuchen Sie, das FlipPad aus- und wieder einzustecken und die Teensy Loader-Software neu zu starten).



*Abbildung 36: Teensy Loader Schritt 3*

Um die Installation der Firmware abzuschließen, wählen Sie “Operation → Reboot”. Sie sollten "Reboot" lesen und das FlipPad sollte kurz piepen.



*Abbildung 37: Teensy Loader Schritt 4*

Um die GUI-Software zu aktualisieren, kopieren Sie die Datei "FlipPadGUI.exe" aus dem Zip-Paket an den gewünschten Ort (und ersetzen damit die alte FlipPadGUI.exe-Datei).

# Erstellen der Firmware

Wenn Sie die Software (Firmware) der FlipPad anpassen möchten, gehen Sie folgendermaßen vor:

1. Kopieren Sie das FlipPad-Repository, https://github.com/asterics/FlipPad
2. Laden Sie die Arduino IDE herunter und installieren Sie sie: https://www.arduino.cc/en/main/software
3. Laden Sie Teensyduino herunter und installieren Sie es: https://www.pjrc.com/teensy/td_download.html
4. Öffnen Sie FLipWare/FLipware.ino mit der Arduino IDE, siehe: https://github.com/asterics/FlipPad/blob/master/FLipWare/FLipWare.ino
5. Verwenden Sie die folgenden Einstellungen in Arduino IDE: o Tools -> Board -> Teensy LC o Tools -> USB Type -> "Serial + Mouse + Keyboard + Joystick" adaptFirmware

*Abbildung 38: Firmware adaptieren*

# Weitere Anleitungen und Fehlerbehebung

Weitere Anleitungen und Fehlerbehebungen finden Sie im [GitHub Wiki des FlipPad-Projekts](https://github.com/asterics/FlipPad/wiki).

# Anhang: Makrobefehle und Tastencodes

## Liste der unterstützten Makrokommandos

| **Kürzel** | **Funktion** | **Beispiel** | | ----------- | ----------------------------------------------------------------------------------------------------------------------------- | --------------------------------------------------------------------------------------------------------------------------------------------- | | CL | Klick linke Maustaste | | | CR | Klick rechte Maustaste | | | CM | Klick mittlere Maustaste (Zahnrad) | | | CD | Doppelklick linke Maustaste | | | HL | Linke Maustaste halten | | | HR | Rechte Maustaste halten | | | HM | Mittlere Maustaste halten | | | TL | Drücken oder Loslassen linke Maustaste (wechseln) | Ändert: gedrückt <-> nicht gedrückt | | TM | Drücken oder Loslassen mittlere Maustaste (wechseln) | | | TR | Drücken oder Loslassen rechte Maustaste (wechseln) | | | RL | Linke Maustaste loslassen | | | RR | Rechte Maustaste loslassen | | | RM | Mittlere Maustaste loslassen | | | WU | Nach unten scrollen | | | WD | Nach oben scrollen | | | MX | Maus horizontal bewegen (x-Achse) | MX 4 -> bewegt Cursor 4 Pixel nach rechts | | MY | Maus vertikal bewegen (y-Achse) | MY -10 -> bewegt Cursor 10 Pixel nach oben | | KW | keyboard write string: Schreibe Wort | KW Hallo! -> schreibt "Hallo!“ am Keyboard | | KP | key press: Keyboard-Tasten drücken (und wieder loslassen). Tasten werden durch Tastenkürzel identifiziert (siehe Liste unten) | KP KEY_UP -> drückt die "Cursor-Up" Taste; KP KEY_CTRL KEY_ALT KEY_DELETE drückt alle 3 Tasten | | KH | key hold: Keyboard-Tasten drücken (und halten) | siehe KP | | KT | key toggle: Zustand der Keyboard-Tasten ändern (drücken wenn nicht gedrückt, loslassen wenn gedrückt) | siehe KP | | KR | key release: Spezifische Tasten auslassen; Tasten werden durch Tastenkürzel identifiziert (siehe Liste unten) | KR KEY_UP -> lässt die „Cursor-Up“ Taste los | | RA | release all = alle Tasten und Mausbuttons loslassen | | | WA | Warten (Millisekunden), bestimmte Anzahl Millisekunden warten | WA 100 -> wartet 100 Millisekunden | | NE | next slot: nächsten Slot laden | | | LO | load slot: Slot per Name laden; wechselt zum angegebenen Slot | LO mouse | | NC | No command: keine Funktion | | | RO <int> | Orientierung des Sticks rotieren | RO 180 -> vertauscht die x- und y-Bewegungen des Sticks/Mundstücks | | JX <int> | Joystick x-Achse setzen | JX 512 -> setzt die x-Achse auf die mittlere Position | | JY <int> | Joystick y-Achse setzen | JY 1023 -> setzt die y-Achse auf die oberste Position | | JZ <int> | Joystick z-Achse setzen | JZ 0 -> setzt die z-Achse auf die niedrigste Position | | JT <int> | Joystick z-Drehung setzen | JT 512 -> setzt die Drehung auf die mittlere Position | | JS <int> | Joystick Regler setzen | JS 512 -> setzt den Regler in die mittlere Position | | JP <int> | Joystick Button drücken | JP 1 -> drückt Joystick button 1 | | JR <int> | Joystick Button loslassen | JR 2 -> drückt Joystick button 2 | | JH <int> | Joystick Hat-Position setzen | JH 45 -> Setzt Joystick Hat auf 45 Grad; Mögliche Werte sind: 0, 45, 90, 135, 180, 225, 270, 315 und -1 zum Einstellen der mittleren Position | | MM <int> | Mausmodus: Cursor ein (int=1) oder alternative Funktionen ein (int=0) | MM1 -> schaltet in den Mausmodus um | | CA | Nullstellung kalibrieren | kalibriert Stick/Mundstück-Mittelstellung | | IP <string> | Infrarot-Kommando abspielen | IP channelUp; gibt den Infrarot-Befehl "channelUp" wieder (wenn dieser IR-Befehlsname aufgezeichnet wurde) |

Bitte beachten Sie, dass bestimmte Befehle zur Anpassung der FlipPad-Einstellungen nicht in dieser Tabelle aufgeführt sind (z. B. Einstellung von Schwellenwerten oder Beschleunigungen, Aufzeichnung von IR-Befehlen usw.). Eine vollständige Liste der Befehle finden Sie in der [FlipPad wiki](https://github.com/asterics/FlipPad/wiki/at-api).

## Liste der Kürzel für Keybord-Tasten

| **Unterstützte Kürzel für Tastaturtasten** | | -------------------------------------------------------------------------------------------------------------------------------------------------------------------------------------------------------------------------------------------------------------------------------------------------- | | **Buchstaben** | | KEY_A  KEY_B  KEY_C  KEY_D  KEY_E  KEY_F  KEY_G  KEY_H  <br/>KEY_I  KEY_J  KEY_K  KEY_L  KEY_M  KEY_N  KEY_O  KEY_P  <br/>KEY_Q  KEY_R  KEY_S  KEY_T  KEY_U  KEY_V  KEY_W  KEY_X KEY_Y KEY_Z | | **Ziffern** | | KEY_1  KEY_2  KEY_3  KEY_4  KEY_5  KEY_6  KEY_7  KEY_8  KEY_9  KEY_0 | | **Funktionstasten** | | KEY_F1  KEY_F2  KEY_F3  KEY_F4  KEY_F5  KEY_F6  KEY_F7  KEY_F8  KEY_F9  KEY_F10  <br/>KEY_F11  KEY_F12  KEY_F13  KEY_F14  KEY_F15  KEY_F16  KEY_F17  KEY_F18  KEY_F19 <br/>KEY_F20  KEY_F21  KEY_F22  KEY_F23  KEY_F24 | | **Navigationstasten** | | KEY_UP  KEY_DOWN  KEY_LEFT  KEY_RIGHT  KEY_TAB  KEY_PAGE_UP  KEY_PAGE_DOWN <br/>KEY_HOME  KEY_END | | **Spezielle Tasten** | | KEY_ENTER  KEY_SPACE  KEY_BACKSPACE  KEY_DELETE  KEY_INSERT  KEY_ESC  KEY_NUM_LOCK<br/>KEY_SCROLL_LOCK  KEY_CAPS_LOCK  KEY_PAUSE<br/><br/>KEY_SEMICOLON  KEY_COMMA  KEY_PERIOD  KEY_MINUS  KEY_EQUAL  KEY_SLASH<br/>KEY_BACKSLASH  KEY_LEFT_BRACE  KEY_RIGHT_BRACE  KEY_QUOTE  KEY_TILDE  KEY_MENU | | **Keypad Tasten** | | KEYPAD_1  KEYPAD_2  KEYPAD_3  KEYPAD_4  KEYPAD_5  KEYPAD_6  KEYPAD_7  KEYPAD_8<br/>KEYPAD_9  KEYPAD_0  <br/>KEYPAD_SLASH  KEYPAD_ASTERIX  KEYPAD_MINUS  KEYPAD_PLUS  KEYPAD_ENTER  KEYPAD_PERIOD | | **Tasten für alternative Funktionen** | | KEY_SHIFT  KEY_CTRL  KEY_ALT  KEY_RIGHT_ALT  KEY_GUI  KEY_RIGHT_GUI |

# Kontakt

Fachhochschule Technikum Wien

Fakultät für Elektrotechnik

Höchstädtplatz 6

A-1200 Wien

ÖSTERREICH

AsTeRICS Foundation

Webpage: [www.asterics-foundation.org](http://www.asterics-foundation.org)

Email: [office@asterics-foundation.org](mailto:office@asterics-foundation.org)

# Haftungsausschluss

Die Fachhochschule Technikum Wien und die AsTeRICS Foundation übernehmen keine Gewährleistung und Haftung für die Funktionsfähigkeit der beschriebenen Geräte, Software und die Richtigkeit der übergebenen Unterlagen.

Weiters haftet die FH TW nicht für gesundheitliche Schäden, die durch die Verwendung der beschriebenen Hard- und Software entstehen. Die Nutzung der bereitgestellten Softwareanwendungen und Hardwaremodule erfolgt auf eigene Gefahr!

# Danksagung

Dieses Projekt wurde teilweise von der Stadt Wien finanziert, Magistratsabteilung für Wirtschaft, Arbeit und Statistik (MA 23), im Rahmen der Projekte AsTeRICS Academy (14-02), ToRaDes (18-04) und Wissensdrehscheibe für Barrierefreie Technologien (26-02)

Logos

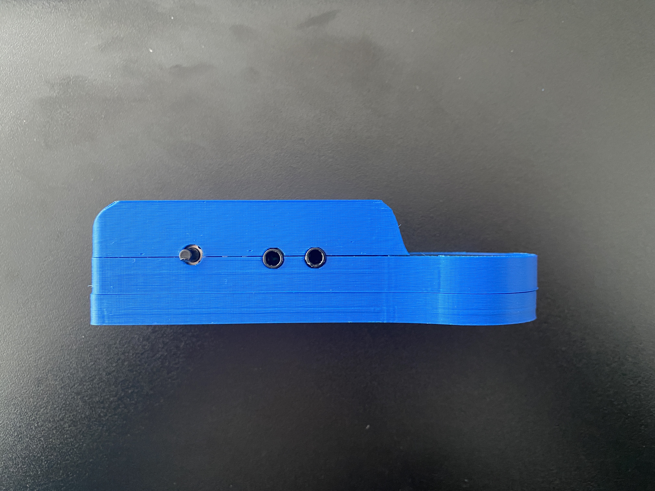
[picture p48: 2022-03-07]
Documentation/UserManual/Bilder/fp-r4.jpg

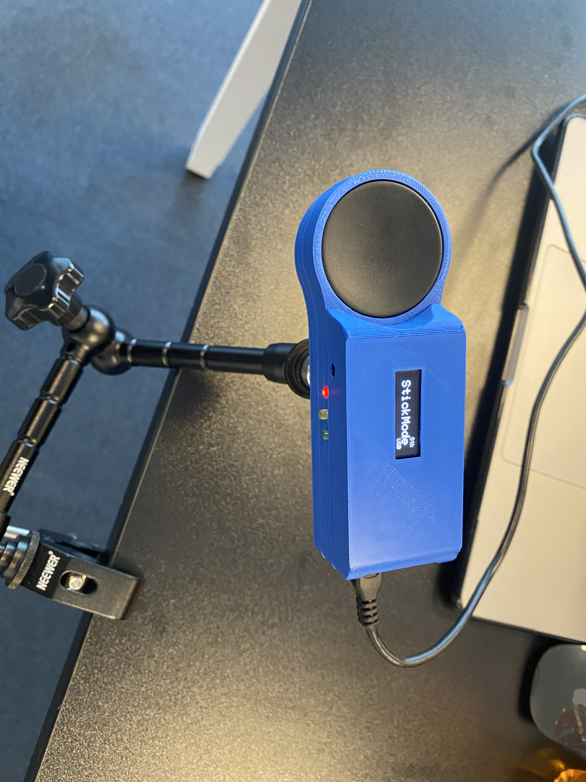
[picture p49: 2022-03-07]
Documentation/UserManual/Bilder/IMG_7118.jpg

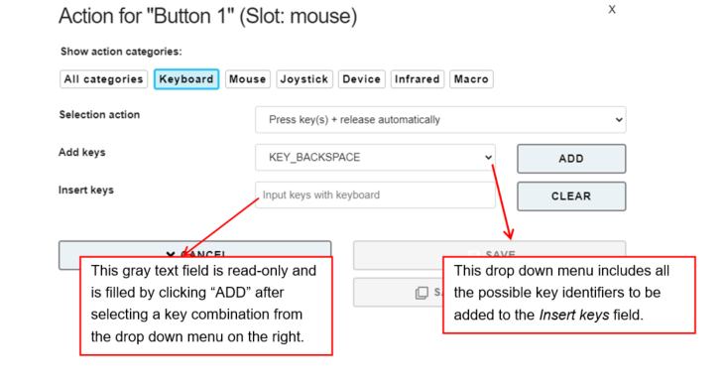
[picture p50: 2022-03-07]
Documentation/UserManual/Bilder/fig8.1.png

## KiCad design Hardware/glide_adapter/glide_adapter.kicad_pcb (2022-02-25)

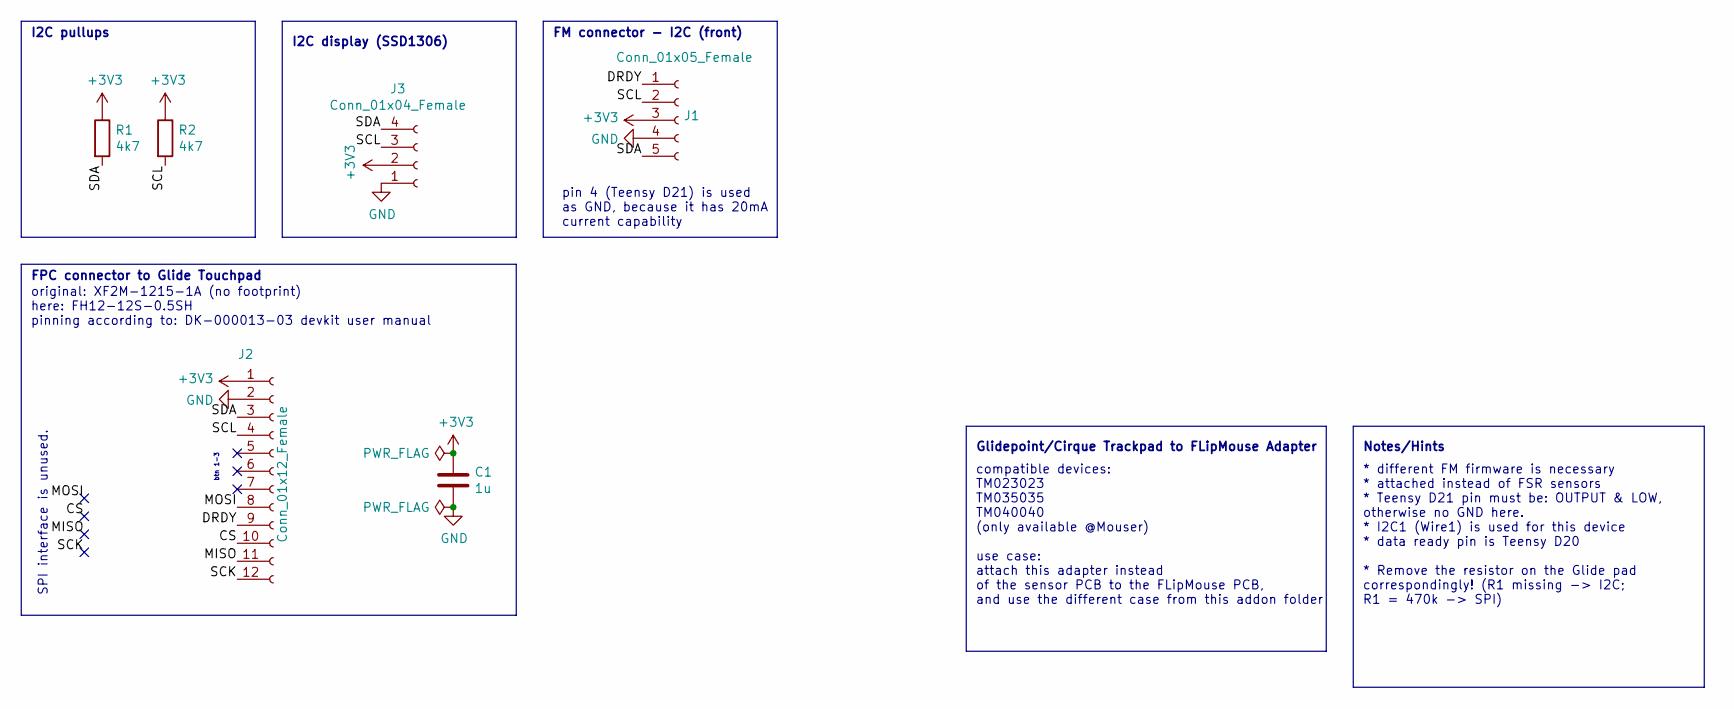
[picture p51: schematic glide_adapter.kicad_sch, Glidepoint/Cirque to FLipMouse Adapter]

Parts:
C1: 1u; C_0805_2012Metric_Pad1.18x1.45mm_HandSolder; Mouser 710-885012207051
J1: Conn_01x05_Female; PinSocket_1x05_P2.54mm_Vertical; Mouser DON'T ORDER (437-8018700510001101)
J2: Conn_01x12_Female; Hirose_FH12-12S-0.5SH_1x12-1MP_P0.50mm_Horizontal; Mouser 798-FH12-12S-0.5SH55
J3: Conn_01x04_Female; Harwin_M20-89004xx_1x04_P2.54mm_Horizontal; Mouser 801-87-004-40-002101
R1: 4k7; R_0805_2012Metric_Pad1.20x1.40mm_HandSolder; Mouser 603-AC0805FR-7W4K7
R2: 4k7; R_0805_2012Metric_Pad1.20x1.40mm_HandSolder; Mouser 603-AC0805FR-7W4K7L

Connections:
+3V3: C1.1, J1.3, J2.1, J2.MP, J3.2, R1.1, R2.1
/CS: J2.10
/DRDY: J1.1, J2.9
/MISO: J2.11
/MOSI: J2.8
/SCK: J2.12
/SCL: J1.2, J2.4, J3.3, R2.2
/SDA: J1.5, J2.3, J3.4, R1.2
GND: C1.2, J1.4, J2.2, J3.1

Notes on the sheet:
FPC connector to Glide Touchpad
Glidepoint/Cirque Trackpad to FLipMouse Adapter
FM connector - I2C (front)
pin 4 (Teensy D21) is used as GND, because it has 20mA current capability
* different FM firmware is necessary * attached instead of FSR sensors * Teensy D21 pin must be: OUTPUT & LOW, otherwise no GND here. * I2C1 (Wire1) is used for this device * data ready pin is Teensy D20 * Remove the resistor on the Glide pad correspondingly! (R1 missing -> I2C; R1 = 470k -> SPI)
original: XF2M-1215-1A (no footprint) here: FH12-12S-0.5SH pinning according to: DK-000013-03 devkit user manual
SPI interface is unused.
I2C pullups
compatible devices: TM023023 TM035035 TM040040 (only available @Mouser) use case: attach this adapter instead of the sensor PCB to the FLipMouse PCB, and use the different case from this addon folder
Notes/Hints
I2C display (SSD1306)
btn 1-3

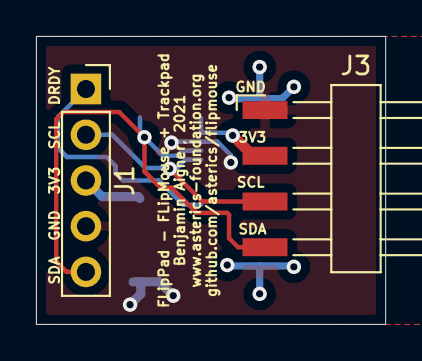
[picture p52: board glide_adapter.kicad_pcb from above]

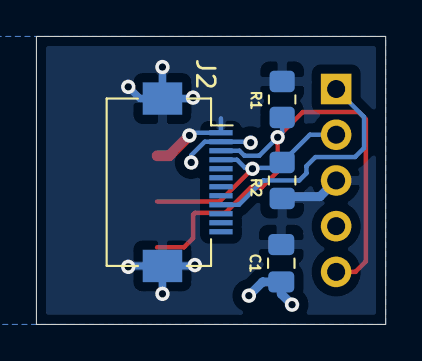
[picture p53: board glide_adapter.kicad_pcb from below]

Board: 2 copper layers, 19.4 x 16.0 mm, 6 parts (4 on the bottom side), 5 nets.

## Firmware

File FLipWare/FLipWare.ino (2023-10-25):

/*
     FLipWare - AsTeRICS Foundation
     For more info please visit: https://www.asterics-foundation.org
     https://github.com/asterics/FLipPad

     Module: FLipWare.ino  (main module)

        This is the firmware for the FLipPad module, 
        it supports HID device emulation via USB and/or Bluetooth via connected sensors and/or serial AT-commands
        For a description of the supported commands see: commands.h

        HW-requirements:
                  TeensyLC with external EEPROM (see board schematics)
                  Cirque Glidepoint Trackpad connected via I2C-2
                  1 pressure sensor connected to ADC pin A0 (optional)
                  3 momentary switches connected to GPIO pins 0,1,2
                  3 slot indication LEDs connected to GPIO pins 5,16,17
                  1 TSOP 38kHz IR-receiver connected to GPIO pin 4
                  1 high current IR-LED connected to GPIO pin 6 via MOSEFT
                  optional: Bluetooth daughter board connected to 10-pin expansion port
                  optional: SSD1306 display (connected via I2C-2)
                  

        SW-requirements:
                  Teensyduino AddOn for Arduino IDE, see https://www.pjrc.com/teensy/td_download.html
                  USB-type set to USB composite device (Serial + Keyboard + Mouse + Joystick)
                  SSD1306Ascii-library by Bill Greiman, see https://github.com/greiman/SSD1306Ascii

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
*/

#include "FlipWare.h"
#include "gpio.h"      
#include "infrared.h"      
#include "cirque.h"        // for Cirque Glidepoint trackpad 
#include "display.h"       // for SSD1306 I2C-Oled display
#include "modes.h"
#include "tone.h"
#include "parser.h"  
#include "reporting.h"
#include "cim.h"
#include "utils.h"         

/**
   device name for ID string & BT-pairing
*/
char moduleName[]="Flippad";   

/**
   default values for empty configuration slot 
*/
const struct SlotSettings defaultSlotSettings = {      // default slotSettings valus, for type definition see fabi.h
  "mouse",                          // initial slot name
  0,                                // initial keystringbuffer length
  1,                                // padMode: Mouse cursor movement active
  40, 40, 20, 20, 50, 20,           // accx, accy, deadzone x, deadzone y, maxspeed, acceleration time
  400, 600, 3,                      // threshold sip, threshold puff, wheel step,
  800, 10,                          // threshold strong puff, threshold strong sip
  40, 20, 40, 20 ,                  // gain and range drift compenstation( vertical, horizontal)
  0, 0,                             // offset x / y
  0,                                // orientation
  1,                                // bt-mode 1: USB, 2: Bluetooth, 3: both (2 & 3 need daughter board))
};


/**
   static variables and data structures for settings and sensor data management
*/
struct SensorData sensorData {        
  .x=0, .y=0, .xRaw=0, .yRaw=0, .padState=0, .pressure=0, 
  .deadZone=0, .force=0, .forceRaw=0, .angle=0,
  .dir=0,
  .autoMoveX=0, .autoMoveY=0,
  .up=0, .down=0, .left=0, .right=0,
  .calib_now=1,    // calibrate zeropoint right at startup !
  .cx=0, .cy=0,
  .xDriftComp=0, .yDriftComp=0,
  .xLocalMax=0, .yLocalMax=0,
  .ignorePressure = 0
};


struct SlotSettings slotSettings;             // contains all slot settings
uint8_t workingmem[WORKINGMEM_SIZE];          // working memory (command parser, IR-rec/play)
uint8_t actSlot = 0;                          // number of current slot
unsigned long lastInteractionUpdate;          // timestamp for HID interaction updates
uint8_t addonUpgrade = BTMODULE_UPGRADE_IDLE; // if not "idle": we are upgrading the addon module

int padX=0,padY=0,padState=0;  // trackpad data

// forward declaration of functions for sensor data processing
void applyDeadzone();


/**
   @name setup
   @brief setup function, program execution starts here
   @return none
*/
void setup() {
  //load slotSettings
  memcpy(&slotSettings,&defaultSlotSettings,sizeof(struct SlotSettings));

  //initialise BT module, if available (must be done early!)
  initBluetooth();

  // iniitialize other peripherals
  Serial.begin(115200);
  delay(1000);  // allow some time for serial interface to come up
  Wire.begin();
  Wire.setClock(400000);  // use 400kHz I2C clock
  initGPIO();
  initIR();
  initButtons();
  initDebouncers();
  init_CIM_frame();  // for AsTeRICS CIM protocol compatibility
  
  pinMode(PRESSURE_SENSOR_PIN,INPUT_PULLUP);
  if(analogRead(PRESSURE_SENSOR_PIN) > 900)
  {
	  sensorData.ignorePressure = 1;
  }

  bootstrapSlotAddresses();   // initialize EEPROM if necessary
  readFromEEPROMSlotNumber(0, true); // read slot from first EEPROM slot if available !

  initBlink(10,25);  // first signs of life!

  cirqueInstalled=initCirque();      // init and activate cirque trackpad module

  setBTName(moduleName);             // if BT-module installed: set advertising name
  
  displayInstalled=displayInit(cirqueInstalled);   // check if i2c-display connected, if possible: init
  displayUpdate();
 
#ifdef DEBUG_OUTPUT_FULL
  Serial.print("Free RAM:");  Serial.println(freeRam());
  Serial.print(moduleName); Serial.println(" ready !");
#endif

  lastInteractionUpdate = millis();  // get first timestamp
}

/**
   @name loop
   @brief loop function, periodically called after setup()
   @return none
*/
void loop() {
	
  //check if we should go into addon upgrade mode
	if(addonUpgrade != BTMODULE_UPGRADE_IDLE) {
    performAddonUpgrade();
    return;
	}

  // handle incoming serial data (AT-commands)
  while (Serial.available() > 0) {
    // send incoming bytes to parser
    parseByte (Serial.read());      // implemented in parser.cpp
  }
  
  // if incoming data from BT-addOn: forward it to host serial interface
  while (Serial_AUX.available() > 0) {
    Serial.write(Serial_AUX.read());
  }

  // get current sensor values
  if(!sensorData.ignorePressure) sensorData.pressure = analogRead(PRESSURE_SENSOR_PIN);
  else sensorData.pressure = 512;
  padState=updateCirquePad(&padX,&padY); 

  // perform periodic updates  
  if (StandAloneMode && ((millis() >= lastInteractionUpdate + UPDATE_INTERVAL) || padState))  {
    lastInteractionUpdate = millis();
    
    // get coordinates and handle tap gestures
    sensorData.xRaw=sensorData.x=padX;
    sensorData.yRaw=sensorData.y=padY;
    sensorData.padState=padState;
    handleTapClicks(padState, slotSettings.gv*10);  // perform clicks and drag actions when in pad mode

    // calculate angular direction and force
    sensorData.forceRaw = __ieee754_sqrtf(sensorData.xRaw * sensorData.xRaw + sensorData.yRaw * sensorData.yRaw);
    if (sensorData.forceRaw !=0) {
      sensorData.angle = atan2f ((float)sensorData.yRaw / sensorData.forceRaw, (float)sensorData.xRaw / sensorData.forceRaw );
      
      // get 8 directions
      sensorData.dir=(180+22+(int)(sensorData.angle*57.29578))/45+1;  // translate rad to deg and make 8 sections
      if (sensorData.dir>8) sensorData.dir=1;  
    }

    // calculate updated x/y/force values according to deadzone
    applyDeadzone();

    handleUserInteraction();  // handle all mouse / joystick / button activities

    reportValues();     // send live data to serial
    updateLeds();
    UpdateTones();
  }

  if (CimMode) {
    handleCimMode();   // create periodic reports if running in AsTeRICS CIM compatibility mode
  }
}


/**
   @name applyDeadzone
   @brief calculates deadzone and respective x/y/force values (in sensorData struct)
   @return none
*/
void applyDeadzone()
{
    //  circular deadzone for mouse control
    if (sensorData.forceRaw != 0) {     
      float a= slotSettings.dx>0 ? slotSettings.dx : 1 ;
      float b= slotSettings.dy>0 ? slotSettings.dy : 1 ;      
      float s=sinf(sensorData.angle);
      float c=cosf(sensorData.angle);
      sensorData.deadZone =  a*b / __ieee754_sqrtf(a*a*s*s + b*b*c*c);  // ellipse equation, polar form
    }
    else sensorData.deadZone = slotSettings.dx;

    sensorData.force = (sensorData.forceRaw < sensorData.deadZone) ? 0 : sensorData.forceRaw - sensorData.deadZone;

    if (slotSettings.padMode!=PADMODE_PAD) { 
      sensorData.x = (int) (sensorData.force * cosf(sensorData.angle));
      sensorData.y = (int) (sensorData.force * sinf(sensorData.angle));
    }
}

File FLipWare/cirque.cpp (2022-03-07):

/*
     FLipWare - AsTeRICS Foundation
     For more info please visit: http://www.asterics-academy.net

     Module: cirque.cpp - implementation of the cirque pinnacle trackpad interface, header file

     Based upon Cirque trackpad demo code, Copyright (c) 2018 Cirque Corp.
     Restrictions apply. See: www.cirque.com/sw-license
     Using a Cirque TM0XX0XX w/ Curved Overlay in I2C-mode,
     make sure that R1 is _not_ populated with a 470k resistor

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
*/

#include <Arduino.h>
#include "FlipWare.h"
#include "cirque.h"
#include "buttons.h"
#include "modes.h"
#include "display.h"

// Hardware pin-number labels
#define SDA_PIN   23
#define SCL_PIN   22
#define DR_PIN    20
#define GND_PIN   21

// Cirque's 7-bit I2C Slave Address
#define SLAVE_ADDR  0x2A

// Masks for Cirque Register Access Protocol (RAP)
#define WRITE_MASK  0x80
#define READ_MASK   0xA0

// Register config values for this demo
#define SYSCONFIG_1   0x00
#define FEEDCONFIG_1  0x03
#define FEEDCONFIG_2  0x1F
#define Z_IDLE_COUNT  0x05

// Coordinate scaling values
#define PINNACLE_XMAX     2047    // max value Pinnacle can report for X
#define PINNACLE_YMAX     1535    // max value Pinnacle can report for Y
#define PINNACLE_X_LOWER  127     // min "reachable" X value
#define PINNACLE_X_UPPER  1919    // max "reachable" X value
#define PINNACLE_Y_LOWER  63      // min "reachable" Y value
#define PINNACLE_Y_UPPER  1471    // max "reachable" Y value
#define PINNACLE_X_RANGE  (PINNACLE_X_UPPER-PINNACLE_X_LOWER)
#define PINNACLE_Y_RANGE  (PINNACLE_Y_UPPER-PINNACLE_Y_LOWER)
#define ZONESCALE 256   // divisor for reducing x,y values to an array index for the LUT
#define ROWS_Y ((PINNACLE_YMAX + 1) / ZONESCALE)
#define COLS_X ((PINNACLE_XMAX + 1) / ZONESCALE)

// ADC-attenuation slotSettings (held in BIT_7 and BIT_6)
// 1X = most sensitive, 4X = least sensitive
#define ADC_ATTENUATE_1X   0x00
#define ADC_ATTENUATE_2X   0x40
#define ADC_ATTENUATE_3X   0x80
#define ADC_ATTENUATE_4X   0xC0

// Convenient way to store and access measurements
typedef struct _absData
{
  uint16_t xValue;
  uint16_t yValue;
  uint16_t zValue;
  uint8_t buttonFlags;
  bool touchDown;
  bool hovering;
} absData_t;

uint8_t dragging = 0;
int dragDistanceX=0,dragDistanceY=0;
uint32_t dragBeginTimestamp = 0;

uint8_t cirqueInstalled = 0;
absData_t touchData;


//const uint16_t ZONESCALE = 256;
//const uint16_t ROWS_Y = 6;
//const uint16_t COLS_X = 8;

// These values require tuning for optimal touch-response
// Each element represents the Z-value below which is considered "hovering" in that XY region of the sensor.
// The values present are not guaranteed to work for all HW configurations.
const uint8_t ZVALUE_MAP[ROWS_Y][COLS_X] =
{
  {1, 1,  1,  1,  1,  1, 1, 1},
  {1, 1,  2,  3,  3,  2, 1, 1},
  {1, 2,  3,  4,  4,  3, 2, 1},
  {1, 2,  3,  4,  4,  3, 2, 1},
  {1, 1,  2,  3,  3,  2, 1, 1},
  {1, 1,  1,  1,  1,  1, 1, 1},
};

/*
  {
  {0, 0,  0,  0,  0,  0, 0, 0},
  {0, 2,  3,  5,  5,  3, 2, 0},
  {0, 3,  5, 15, 15,  5, 2, 0},
  {0, 3,  5, 15, 15,  5, 3, 0},
  {0, 2,  3,  5,  5,  3, 2, 0},
  {0, 0,  0,  0,  0,  0, 0, 0},
  };
*/

void Pinnacle_EnableFeed(bool feedEnable);
void Pinnacle_ClearFlags();

/*  RAP Functions */

int RAP_Init()
{
  delay(200);
  // Set up I2C peripheral
  Wire1.begin();
  //  Wire1.setDefaultTimeout(10000); // 10ms
  Wire1.setSDA(SDA_PIN);
  Wire1.setSCL(SCL_PIN);
  Wire1.setClock(100000);
  Wire1.beginTransmission(SLAVE_ADDR);
  return (Wire1.endTransmission());
}

// Reads <count> Pinnacle registers starting at <address>
void RAP_ReadBytes(byte address, byte * data, byte count)
{
  uint8_t cmdByte = READ_MASK | address;   // Form the READ command byte
  uint8_t i = 0;

  Wire1.beginTransmission(SLAVE_ADDR);   // Set up an I2C-write to the I2C slave (Pinnacle)
  Wire1.write(cmdByte);                  // Signal a RAP-read operation starting at <address>
  Wire1.endTransmission(true);           // I2C stop condition

  Wire1.requestFrom((uint8_t)SLAVE_ADDR, count, (uint8_t)true);  // Read <count> bytes from I2C slave
  while (Wire1.available())
  {
    data[i++] = Wire1.read();
  }
}

// Writes single-byte <data> to <address>
void RAP_Write(byte address, byte data)
{
  uint8_t cmdByte = WRITE_MASK | address;  // Form the WRITE command byte

  Wire1.beginTransmission(SLAVE_ADDR);   // Set up an I2C-write to the I2C slave (Pinnacle)
  Wire1.send(cmdByte);                   // Signal a RAP-write operation at <address>
  Wire1.send(data);                      // Write <data> to I2C slave
  Wire1.endTransmission(true);           // I2C stop condition
}



/*  ERA (Extended Register Access) Functions  */
// Reads <count> bytes from an extended register at <address> (16-bit address),
// stores values in <*data>
void ERA_ReadBytes(uint16_t address, uint8_t * data, uint16_t count)
{
  uint8_t ERAControlValue = 0xFF;

  Pinnacle_EnableFeed(false); // Disable feed

  RAP_Write(0x1C, (uint8_t)(address >> 8));     // Send upper byte of ERA address
  RAP_Write(0x1D, (uint8_t)(address & 0x00FF)); // Send lower byte of ERA address

  for (uint16_t i = 0; i < count; i++)
  {
    RAP_Write(0x1E, 0x05);  // Signal ERA-read (auto-increment) to Pinnacle

    // Wait for status register 0x1E to clear
    do
    {
      RAP_ReadBytes(0x1E, &ERAControlValue, 1);
    } while (ERAControlValue != 0x00);

    RAP_ReadBytes(0x1B, data + i, 1);

    Pinnacle_ClearFlags();
  }
}

// Writes a byte, <data>, to an extended register at <address> (16-bit address)
void ERA_WriteByte(uint16_t address, uint8_t data)
{
  uint8_t ERAControlValue = 0xFF;

  Pinnacle_EnableFeed(false); // Disable feed

  RAP_Write(0x1B, data);      // Send data byte to be written

  RAP_Write(0x1C, (uint8_t)(address >> 8));     // Upper byte of ERA address
  RAP_Write(0x1D, (uint8_t)(address & 0x00FF)); // Lower byte of ERA address

  RAP_Write(0x1E, 0x02);  // Signal an ERA-write to Pinnacle

  // Wait for status register 0x1E to clear
  do
  {
    RAP_ReadBytes(0x1E, &ERAControlValue, 1);
  } while (ERAControlValue != 0x00);

  Pinnacle_ClearFlags();
}



/*  Pinnacle-based TM0XX0XX Functions  */
int Pinnacle_Init()
{
  if (RAP_Init()) return (0);
  pinMode(DR_PIN, INPUT);

  // Host clears SW_CC flag
  Pinnacle_ClearFlags();

  // Host configures bits of registers 0x03 and 0x05
  RAP_Write(0x03, SYSCONFIG_1);
  RAP_Write(0x05, FEEDCONFIG_2);

  // Host enables preferred output mode (absolute)
  RAP_Write(0x04, FEEDCONFIG_1);

  // Host sets z-idle packet count to 5 (default is 30)
  RAP_Write(0x0A, Z_IDLE_COUNT);
  return (1);
}
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

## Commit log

2022-02-25 added FlipPad V1.0
    [case_TM035035-base.stl, case_TM035035-bottom.stl, case_TM035035-top.stl, case_TM035035.FCStd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]
2022-02-26 easier-to-use default settings without finger gestures, added seperate demo settings with enabled finger gestures
2022-02-28 Added BOM
    [FLipPad_BOM.xls]
2022-02-28 Changed hotshoe position & changed 3D file directory; added link to CManual sources
    [case_TM035035-base.stl, case_TM035035-bottom.stl, case_TM035035-top.stl, case_TM035035.FCStd]
2022-02-28 Removed unused things from the FreeCAD project, moved raytracing & animation project to the repo for the construction kit.
    [case_TM035035.FCStd]
2022-03-04 Added case design for bigger (TM040040) trackpad
    [case_TM040040-base.stl, case_TM040040-bottom.stl, case_TM040040-top.stl, case_TM040040.FCStd]
2022-03-07 Added TOM formatted BOM list
    [FLipPad_BOM_TOM_format.xls]
2022-03-07 small changes
    [FLipPad_BOM_TOM_format.xls]
2023-04-05 updated Readme for PCB
2023-04-25 changed orientation of Oled Display for shorter trackpad cable length
2023-07-24 Added a check on startup if an analog sensor is connected; ignore readings if not

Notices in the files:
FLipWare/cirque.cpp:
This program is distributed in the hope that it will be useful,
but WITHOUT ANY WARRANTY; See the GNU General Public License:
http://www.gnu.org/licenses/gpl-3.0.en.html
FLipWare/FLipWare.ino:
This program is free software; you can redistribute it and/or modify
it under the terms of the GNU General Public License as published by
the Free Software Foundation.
